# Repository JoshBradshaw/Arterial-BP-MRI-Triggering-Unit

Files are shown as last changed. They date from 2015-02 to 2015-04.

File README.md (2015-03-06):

# Arterial-BP-MRI-Triggering-Unit
Full source code and schematics for an Arterial Blood Pressure Pulse MRI triggering unit

A full description of each major component of this project is available at the [project website](http://joshbradshaw.github.io/Arterial-BP-MRI-Triggering-Unit/)

# This device is an arterial blood presure triggering unit for retrospective gating in MRI imaging.

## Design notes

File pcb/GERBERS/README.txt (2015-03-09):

*.CMP = Top or Component Side
*.SOL = Bottom or Solder Side
*.SLK/PLC = Top/Bottom Component Legend
*.?MK/ST? = Top/Bottom Solder Mask
*.DRD = NC Drill File
*.DRL = Tool Report (sample)
NC Drill File sample	3.3 Leading Zeros is typical

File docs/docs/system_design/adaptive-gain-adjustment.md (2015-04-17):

## Variable Gain Amplifier with SPI Interface

The analog output signal provided by the Samba Sensor’s pressure measurement system had a very small amplitude compared to the full scale range of the analog to digital converter, so an amplifier was required to increase the signal closer to the full scale range of the ADC. 

Unfortunately, the blood pressure of fetal pigs has never been measured from the carotid artery, so it was impossible to determine the correct gain value for the amplifier in advance. This problem was further confounded, because the effect of our chosen anaesthetic on fetal blood pressure was also unknown. To deal with this problem, I opted to build a variable gain amplifier, with an automatic feedback system to maintain a consistent signal amplitude throughout the experiment. A simplified schematic variable gain amplifier circuit is shown below.

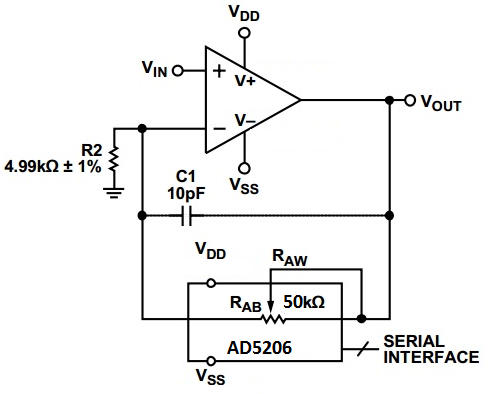
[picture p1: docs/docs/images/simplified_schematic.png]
Simplified schematic


This circuit uses a precision operational amplifier, with a digital potentiometer (AD5206) in the feedback path to allow the gain to be adjusted by the microcontroller as required. The digital potentiometer has 256 counts, giving the amplifier an adjustable gain range of 1-11x. This is sufficient for even the lowest possible fetal blood pressures.

## Algorithm for Gain Adjustment on the Fly

The input of the gain adjustment is a sample from the ADC taken every 100ms. While each sample is recorded, the algorithm compares it to the minimum signal magnitude and maximum magnitude threshold which are 1/5 and 4/5 of the ADC’s full scale range, respectively. After a five second windowing period, the signal amplitude is compared against the thresholds, to see if any gain adjustment is required. The three possible cases:

1.	Signal failed to exceed minimum magnitude threshold during the five second window.
2.	Signal exceeded maximum the maximum magnitude threshold during the five second window.
3.	The signal exceeded the minimum magnitude threshold, and did not exceed the maximum threshold.
    In case one, the gain adjustment algorithm gradually increases the gain during each windowing period, as shown in the figure below. The gain increase stops when the signal exceeds the threshold. Same process occurs in reverse for case three. The algorithm is illustrated in the flow chart below.

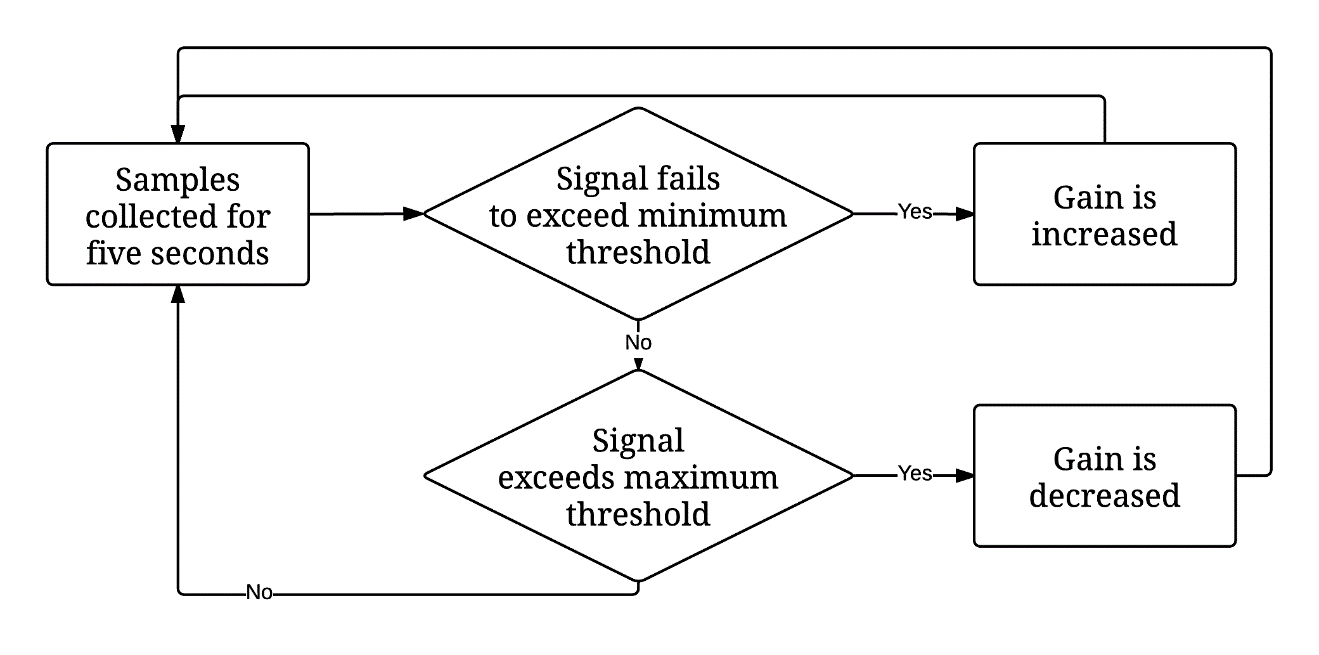
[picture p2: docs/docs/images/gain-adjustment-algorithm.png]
Gain adjustment algorithm flow chart


The actual functioning of the gain adjustment algorithm is illustrated in the plot below. In this test, the triggering system was connected to a function generator which produced a blood pressure waveform with a peak to peak voltage of 700mV. This signal amplitude is based upon recordings on fetal lambs with an identical transducer. As you can see, the gain is very gradually increased in such a manner that it does not disrupt the triggering algorithm, which operates perfectly throughout the duration of the gain increase.

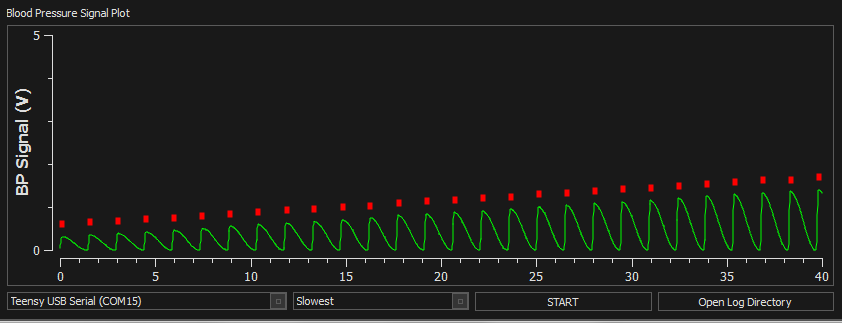
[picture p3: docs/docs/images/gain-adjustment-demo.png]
Gain adjustment demo plot


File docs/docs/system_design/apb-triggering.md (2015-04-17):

## Blood Pressure Signal Preprocessing

The top plot in Figure xx shows an arterial blood pressure waveform which was measured invasively in a fetal lamb. Notice that the notice after the main pressure peak, there is a second reflection peak, which results from closing of the aortic value. 

This waveform is relatively noisy, and the peak is not particularly easy to identify. For this reason, it is necessary to apply a filtering algorithm to simplify peak detection. First a first order low pass filter with a cut-off frequency of 25Hz is applied, to smooth the small spikes in the pressure waveform, as shown in the figure below. The first order low pass filter’s equation is given below.

low pass filter

Next the slow sum function is applied. The slope sum function is defined as:

low pass filter

Where the optimal value of the windowing constant k is the number of samples in the rising edge of the signal [2]. For the fetal pig application, we chose k=15, based upon visual inspection of pre-existing fetal lamb blood pressure recordings, which are very similar to fetal pigs in terms of blood pressure and heart rate. 
The plot below illustrates shows a plot of a fetal lamb’s blood pressure, and the corresponding slope filtered output for that blood pressure waveform. 

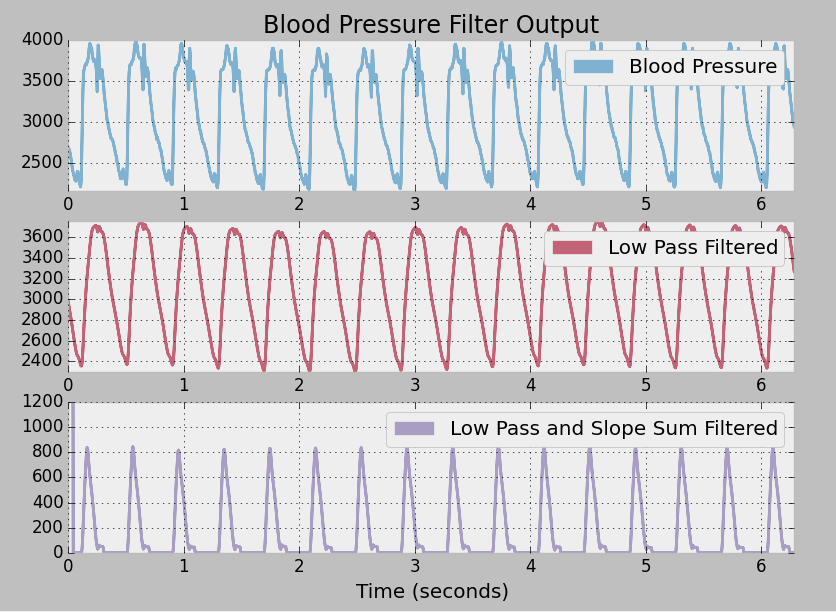
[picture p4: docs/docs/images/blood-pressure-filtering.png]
low pass filter


Notice that the low pass filter removes the high frequency ridges from the blood pressure waveform, leaving only the low frequency content that corresponds to the expansion and contractions of the hearts ventricles. 

The slope sum function improves the signal by establishing a consistent baseline of zero, eliminating the effects of DC drifts in the measurement instrument. The slope sum function also sharpens the peaks, which makes the problem of automatic peak detection far less ambiguous.

## Testing

The algorithm was evaluated against the following test blood pressure waveforms.

1. [MIT Database of non-invasive blood pressure recordings](http://physionet.cps.unizar.es/physiobank/database/slpdb/slpdb.shtml)
2. Pulse oximeter of my own heart, taken while serving as test subject for a maternal health sequence.
3. Invasive fetal lamb blood pressure recordings, taken by an Australian research group.

## Blood Pressure Peak Detection

The blood pressure pulse detection algorithm is a state machine. The high level overview of the algorithm is given by the flow chart below.

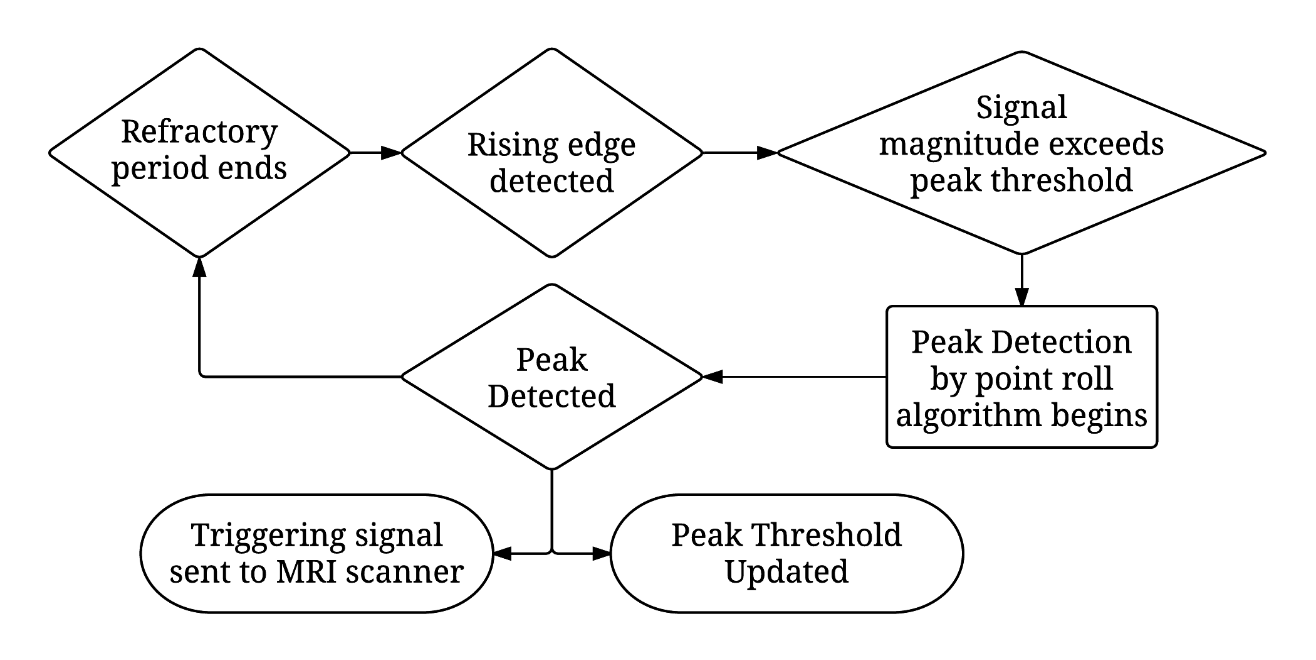
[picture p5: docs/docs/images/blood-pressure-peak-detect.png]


To ensure that the peak detector only triggers on unique blood pressure pulses, a refractory period is applied between peaks, and the algorithm does not begin peak detection until the rising edge is detected and the signal magnitude is greater than the peak threshold. The peak threshold is calculated as ½ of the average of the last five peaks.

The point roll algorithm for peak detection works by comparing the value of the current sample to the value (u[n]) of the fourth more recent sample (u[n-4]). This operation is similar to the backwards approximation of the first derivative. A peak is detected when u[n-4] > u[n], which corresponds to a slow of zero.

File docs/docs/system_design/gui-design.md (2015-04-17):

## Signal Monitoring Tool

The blood pressure triggering device needs to have an interface so that the researcher operating it can tell whether it is functioning properly. The interface must provide the operator with near real-time feedback on the signal level of the pressure sensor, and the timing of the trigger pulses. The interface should provide the researcher with an easy way to export the pressure data for further analysis, and should be sufficiently simple to install on a new computer that it can be quickly transferred via USB key or network drive to a different computer.

The tool is based entirely on [this excellent project](http://www.swharden.com/blog/2013-05-08-realtime-data-plotting-in-python/). All I did was modify the form, integrate the python serial library to get the sensor values from the Teensy over Serial, and add a couple of buttons and menus to control everything. All told, it only amounted to about one day of work. Finally, I used py2exe to make it into a portable application, so that it can be run on any of the computers on the scan room without having to worry about setting up a python environment.

Here's an image of the finished monitoring tool in action.

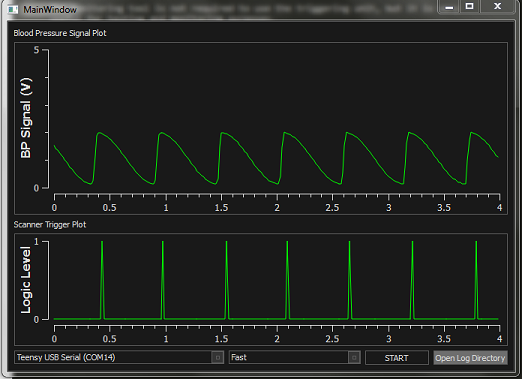
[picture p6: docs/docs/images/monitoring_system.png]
Monitoring System
 

### Setup

There are two ways to run the monitoring tool:

1. On windows you can run the pre-built executable: [monitoring_tool_win32_v1.0.zip](https://drive.google.com/file/d/0B9S2t7PTl3ecVFlvSmQzb3l2UDQ/view?usp=sharing)

2. If that executable doesn't work, the full development environment I built this with can easily be installed. Just download [PythonXY](https://code.google.com/p/pythonxy/), download the the [source code](https://github.com/JoshBradshaw/Arterial-BP-MRI-Triggering-Unit/), navigate to the monitoring_tool directory in terminal and run the program with 

	$ python realtimePlot.py

If you aready have a python 2.X development environment and you don't want to install PythonXY over it, use pip to install pyQt and pySerial.

NOTE: Mac OSX support has not been tested, but this program will most likely run fine on Macs as long as you run from source code (the pre-compiled binary will not work)

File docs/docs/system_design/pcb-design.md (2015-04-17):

## PCB Design

I opted to design a simple PCB for this project, so that more versions of this triggering unit can be produced with minimal effort. 

### Design Criteria

1. Analog ground plane must be completely separated from the digital groundplane to avoid crosstalk on the sensitive analog amplification circuits.
2. Must use 10/10 thou minimum trace width and clearance, so that this board can easily be manufactured by anyone.
3. Must meet the weird drill size restrictions of [APcircuits](http://apcircuits.com/), because they've the only vendor I've who will ship a few boards to SickKids on a quick turnaround for a reasonable price.
4. Must use parts with >1mm pin pitch, so that it can easily be hand assembled by novices.

For anyone wishing to build this board, some moderate to advanced soldering is required. You can do it with very little experience, just follow this tutorial: [Sparkfun SMD soldering tutorial](https://www.sparkfun.com/tutorials/96). Make sure you buy top quality flux, solder and tweezers!

The Teensy eagle CAD library used in this design is available at the [PJRC website](https://www.pjrc.com/teensy/eagle_lib.html). 

### PCB Manufacture

For PCB prototyping, I went with [APcircuits](http://apcircuits.com/). 

Getting one of these boards manufactured is as simple as uploading the GERBER files (included in the git repository) to a manufacturer's website.

### Design:

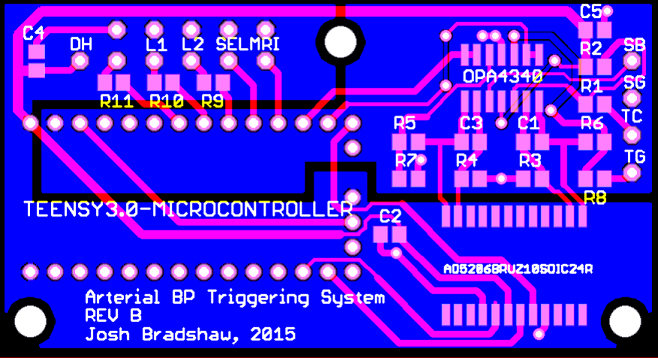
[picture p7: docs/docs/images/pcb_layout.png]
Circuit board layout


### Bare Board:

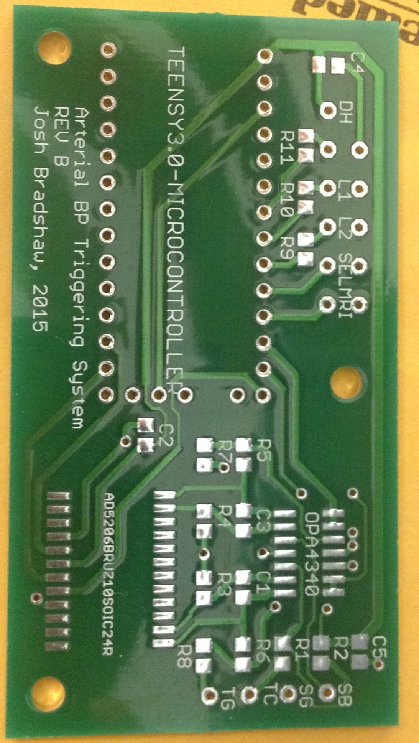
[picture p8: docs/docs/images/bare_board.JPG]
Circuit board layout


### Assembled Board:

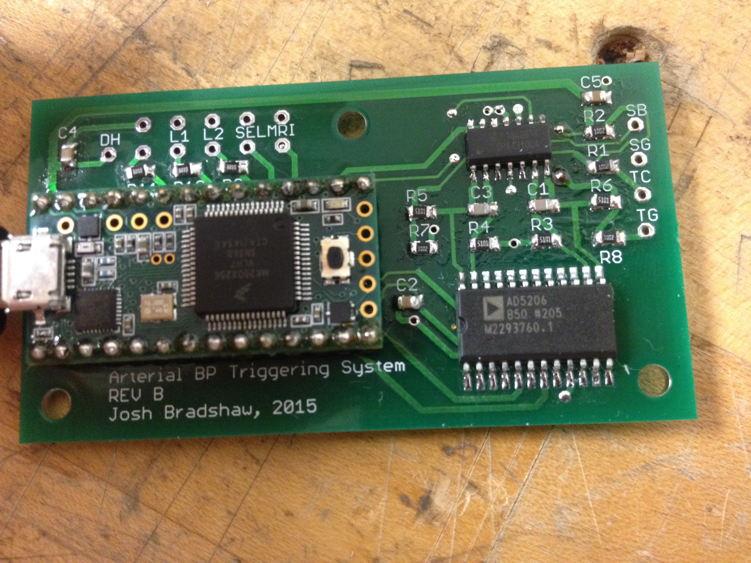
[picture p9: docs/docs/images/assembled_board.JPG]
Circuit board layout


### Things to fix in subsequent revisions

1. One sub-optimal choice I made in the design process of this PCB was the decision to use a 6 channel digital potentiometer, when I'm currently only using two channels. I chose that part simply because I did the breadboard verion with a six channel pot, and because digikey didn't have the 2 or 4 channel version of the part in stock while I was putting the prototype together.

### Related Questions and Uncertainty
1. How much electromagnetic inferferance from the MRI machine will the instruments be exposed to when they're sitting in the control room of the 3T scanner, assuming that we scan with the door closed and the waveguide plugged with a conductive blanket?

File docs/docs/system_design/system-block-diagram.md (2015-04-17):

## System Block Diagram

The blood pressure signal is collected by an optical pressure transducer, which is inserted into the fetal pig’s carotid artery. The optical blood pressure signal is converted into an analog electrical signal by the pressure measurement module (see Appendix A for details), which is then amplified by the variable gain amplifier and measured by the analog to digital converter. 

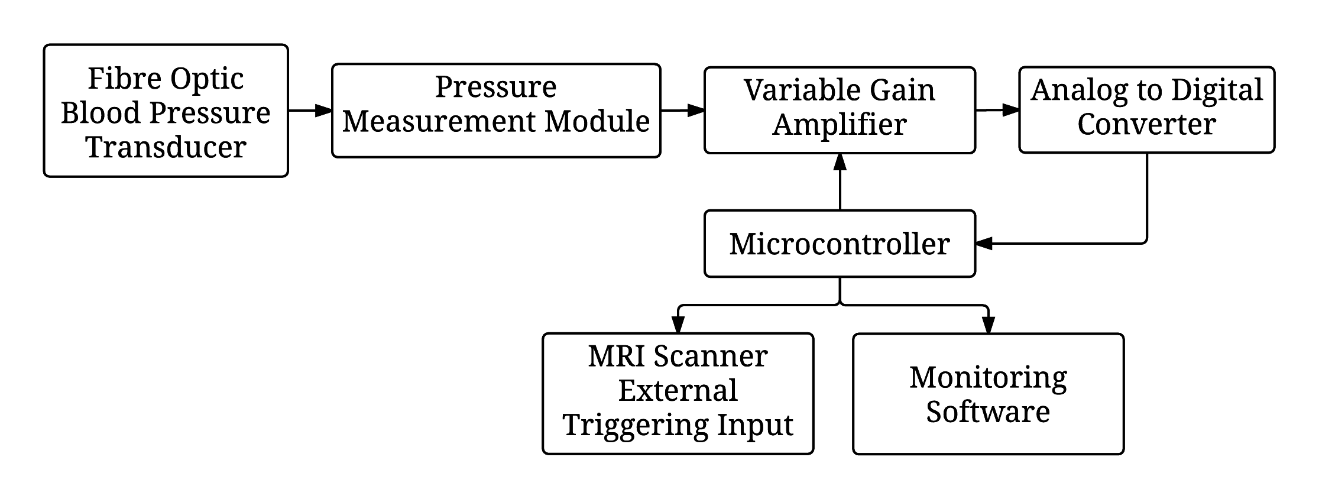
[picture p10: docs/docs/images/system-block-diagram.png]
System block diagram


The microcontroller uses a variety of digital signal processing algorithms to filter the signal and detect the pig’s pulse. Each time a heartbeat is detected, a triggering signal is sent to the MRI scanner, and a signal is sent to the monitoring software so that the experimenter can verify that the triggering signal was sent at the correct instant.

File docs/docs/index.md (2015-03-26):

## System Overview

<style>
td { 
  border: solid;
  border-width: 1px 1px;
  padding: 5px;
}
</style>

The Arterial Blood Pressure Triggering System is an open source tool developed at SickKids. The system converts a blood pressure signal into a TTL signal, as illustrated below.

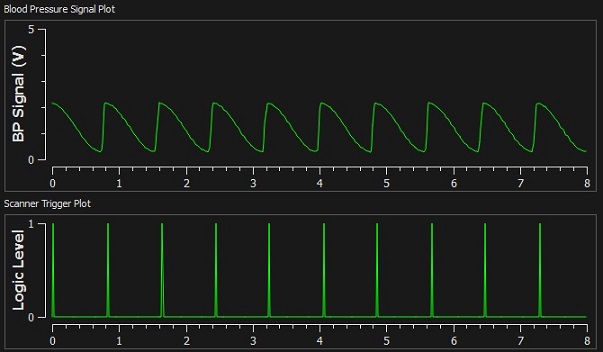
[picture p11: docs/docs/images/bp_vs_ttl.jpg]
illustration of how the triggering system transforms blood pressure signal into TTL signal


This is useful for situations in which a gating signal is required to correct for pulsatile flow or cardiac motion, but the standard clinical ECG or pulse oximeter based triggering systems can not be used. The original application of this system was to provide a retrospective gating signal during 4DFlow and phase contrast scans on prenatal Yorkshire pig fetus's hearts. During the experiments, the fetal pigs blood pressure was monitored using an invasive Samba flow probe in the carotid artery.

### Key Features

* Compatible with [Transonic](http://www.transonic.com/products/research/product/t402t403-multi-channel-research-consoles/) and Samba Sensors pressure measurement modules, and can easily be adapted to work with most other pressure measurement instruments
* Unit calibrates itself automatically every three seconds to correct for baseline drift, and large changes in maximum signal amplitude
* Performs well even on noisy and irregular blood pressure waveforms
* Plug-and-play operation with a one second boot time
* The triggering unit has voltage regulation circuitry complete with inline fuses, to ensure that the scanner will be protected in the event of an electrical fault in the computer or pressure measurement instrument
* Simple monitoring software shows real-time plots of the blood pressure and triggering waveforms, and logs that data so that it can be compared against the scan data in post processing

### Hardware

The triggering unit is shown below:

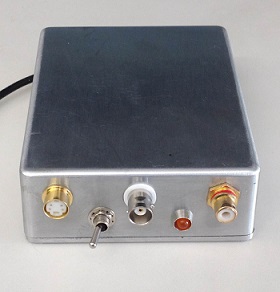
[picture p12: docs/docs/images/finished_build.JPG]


The connections on the front panel of the triggering unit are:

<table>
	<tr>
		<td>Samba Sensor Input (s-video)</td>
		<td>Transonic Sensor Input (BNC)</td>
		<td>External Trigger Out (RCA)</td>
	</tr>
	<tr>
		<td>Input Selection Switch</td>
		<td></td>
		<td>Trigger Status LED</td>
	</tr>
</table>
<br />
Finally, a USB cable runs out of the back corner of the unit. This cable is connected to a computer to power the unit, and optionally to transfer the blood pressure readings to the monitoring software.

## Monitoring Software

triggering unit photo

The monitoring tool give the experimenter real-time feedback on the pressure catheter and the triggering signal. The top chart animation shows the input signal from the pressure catheter, and the bottom chart animation shows the triggering signal that's been sent to the scanner. These charts are updated in real-time with <20ms of delay, so you'll be aware of any irregular heartbeats, or problems with the pressure catheter, right as they happen. Every run of the triggering unit is logged with time and date stamps, so it can be compared with the MRI data in post processing if required.

For more information about the monitoring software see:
1. Monitoring software design

### Scanner compatibility

The SickKids research MRI scanner is the Siemens Magnetom Trio with a field strength of 3T, so the triggering unit's TTL output is calibrated to meet or exceed all of the parameters given in Siemen's timing diagram (taken from the latest version of the Magnetom Trio operating manual). The TTL pulses sent by the unit are 20ms in duration at 3.3V, which should be sufficient for most MRI scanners.

### How to aquire a unit

So far only two of these units have been built, and they were both hand assembled. If you're moderately competant with software and electronics you can build one yourself using the schematics. The parts are listed in the schematics directory, and all of the components are avaialble from digikey. For the PCB board, I may be able to provide you one of my spares. Failing that, you can easily send the GERBER files to any circuit board manufacturer to have them assembled.

Feel free to email me at joshbradshaw11@gmail.com if you are interested in adapting this unit to work with a different blood pressure instrument, or want to commision me to build one for you.

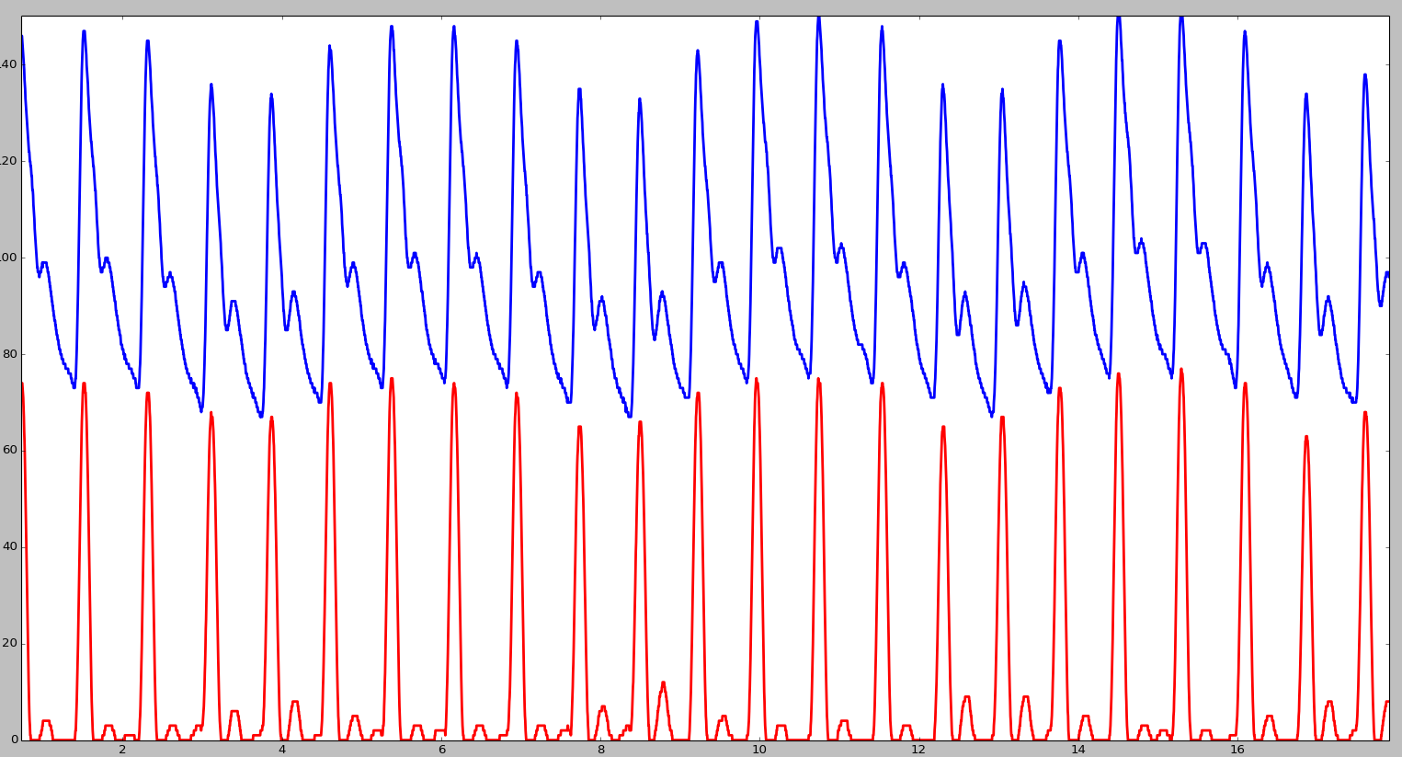
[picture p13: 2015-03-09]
docs/docs/images/ssf_demo.png

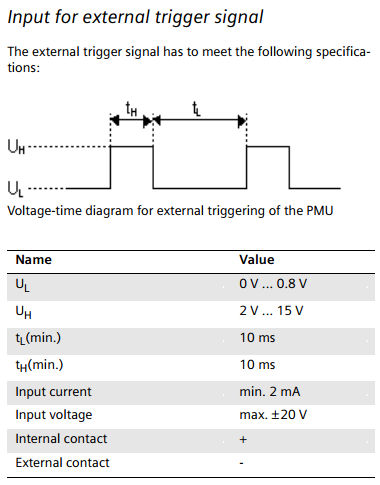
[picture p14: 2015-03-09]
docs/docs/images/siemens_external_trigger (1).png

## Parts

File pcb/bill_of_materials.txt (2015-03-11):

Teensy 3.1 from pjrc.com with header pins
(you can easily solder your old 0.1" headers on if you wish)

part: AD5206BRZ50 package: SOIC-24 quantity: 1
part: OPA4340UA/2K5 package: SOIC-14 quantity: 1

part: 5.1k surface mount resistor package: 0805 quantity: 4
part: 10k surface mount resistor package: 0805 quantity: 4
part: 681 ohm surface mount resistor package: 0805 quantity: 3
part: 10pF surface mount capacitor package: 0805 quantity: 2
part: 0.1uF surface mount capacitor package: 0805 quantity: 3

Other parts (I got these at the hardware store)
A case or project box
SPDT switch
LEDs (must be <3.3V and >5mA max current)
BNC, SVIDEO, RCA connectors (or whatever suits your equipment best)

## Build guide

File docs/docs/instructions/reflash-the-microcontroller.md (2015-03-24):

## How to Reflash the Microcontroller

If for any reason the triggering unit stops working, or requires a software change, you will need to re-flash the Teensy microcontroller. 

To do so:

Install Arduino: [http://arduino.cc/en/Main/Software](http://arduino.cc/en/Main/Software) (I used version 1.6.1)

Install TeensyDuino: [https://www.pjrc.com/teensy/td_download.html](https://www.pjrc.com/teensy/td_download.html)

Connect the triggering unit to your computer's USB port.

Open Windows Device manager and find the Teensy. You will typically find it under ports. 

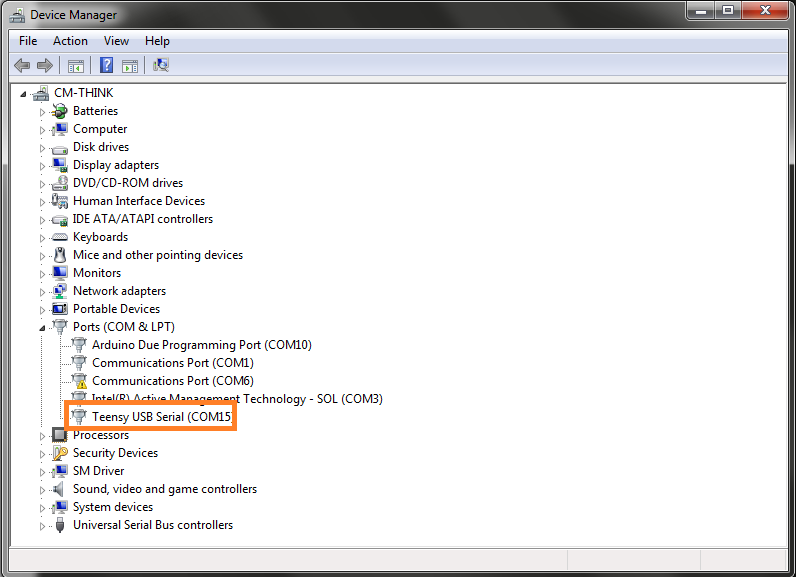
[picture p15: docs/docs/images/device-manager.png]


Note down the COMPORT number (in this case its 15)

Down the source code for the unit from github: [Arterial-BP-MRI-Triggering-Unit](https://github.com/JoshBradshaw/Arterial-BP-MRI-Triggering-Unit)

Next open the Arduino software and open the pressure_trigger_module.ino sketch.

Now you can push your changes to the Teensy microcontroller by pressing VERIFY and then UPLOAD.

Usually this is all you have to do, but sometimes the Teensy requires a manual reset and the software will tell you so by giving you a red error message on the console. If that happens, open the aluminum case (theres a screwdriver that fits perfectly in my drawer) and press the little black button on the teensy board.

If you need to modify my source code there to plenty of resources on the Arduino forum and the Teensy support forum. The language used to program the Arduino boards is essentially C++, without exceptions and other advanced features. 

Note: The contents of the ".ino" file are compiled differently from the .cpp and .h files. Arduino attempts to automatically generate the header file, and this can lead to difficult to understand compilation errors if you use features like classes in this particular source file. For this reason, I recommend putting nothing more than setup(), main() and very basic functions in the ".ino" file.

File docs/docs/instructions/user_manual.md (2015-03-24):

## User Manual

### Setup for Testing with the Analog Function Generator

USE CAUTION! The function generator's output can go up to 20V, which is enough to destroy the pressure trigger module. 
To use it safely:

1. Set the amplitude to minimum and tape it down. Optionally, you can pull the knob out to drop the function generator into the millivolts range.
2. The offset is a little bit tricky to set, because this particular function generator sucks and the offset drifts noticeably from day to day. Pull the knob out engage the switch, and start by setting it to about halfway between 12:00 and 1:00. You can tweak it by a smidgen later to get it just right.
3. To get the waveform looking as close to a arterial blood pressure pulse as possible, set the function to SINE WAVE the frequency range to 10Hz, pull the symmetry knob out to engage it and twist counter-clockwise to the stop. Finally, set the frequency selector knob to 0.2 (for 120 BPM), and leave sweep turned off.
4. At this point you can either use the BNC -> S-video adapter that I made to connect to the Samba input, or a standard BNC cable to connect to the Transonic input.
5. Follow steps 7-9 of the Samba instructions and test the device.

The photo below illustrates the setup, as well as the correct positioning of the knobs on the function generator.

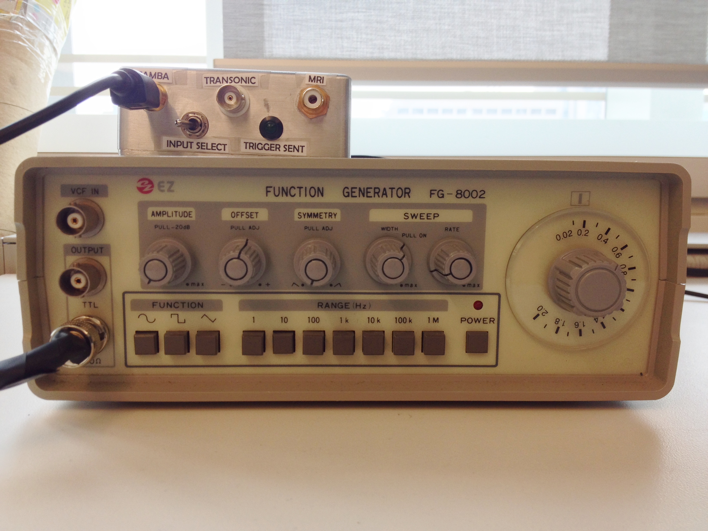
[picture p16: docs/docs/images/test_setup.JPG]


### Setup for Samba 202 Pressure Measurement System

If this is your first time handling the Samba probes, take the time to read the relevant sections of the Samba user manual (included in the box). For invasive measurements you will require distiled and de-ionized water for cleaning the transducer tip, which you can obtain from the wet lab on the 8th floor of the Peter Gilgan Center for Research and Learning (the dispenser is a blue nozzle attached to the main sink). Sterile glassware is available in the hallway that separates the dry lab from the wet lab, you're free to take what you need as long as you return it to the same station for washing.

1. Power up the Samba 202, it will take 1-3 minutes to stabilize the internal temperature.
2. Connect the Samba pressure sensor to channel TWO of the pressure measurement system. Press firmly, because hearing a click does not necessarily mean that a good connection has been made. Be very careful to only handle the blue plastic connector and not the black stress relief on the cable. The fragility of these sensors can not be overstated. The reason we have to use channel two is that channel one is unreliable for unknown reasons, connector contamination is a possibility.
3. Once the Samba unit recognizes the transducer press 1 to zero the transducer. The transducer should be zeroed in free air so that both the low and high blood pressures will give a positive pressure reading.
4. At this point the Samba unit should be working properly and continuously measuring pressure. If you encounter a bad connection error or something along those lines check the manual for instructions. Now is the ideal time to insert the pressure transducer into the test subject.
5. Connect the analog output of the Samba pressure sensor to the pressure trigger module using the S-Video cable provided (this cable has a transparent housing). The connection is labeled SAMBA.
6. Ensure that the INPUT SELECT toggle switch is in the left position (facing the SAMBA input connector).
7. Use the 25ft RCA cable to connect the trigger unit to the external trigger input on the MRI scanner. The external trigger input is on the left side of the scanner, and is marked with a little arrow directed inwards.
8. Plug the USB cable attached to the pressure trigger module to a computer. Ensure that the computer is plugged in (not just running on battery). This is important, because not all laptops maintain a steady 5V USB voltage when they're running on battery power.
9. Launch "realtimePlot.exe" on the computer.
10. Use the serial port selector (dropdown menu on bottom left corner) and choose the port called Teensy USB Serial.
11. Press Start and watch to see whether the system is triggering as expected.

The photo below illustrates most of the connections that you will need to make, as well as the screen that you should see when the Samba pressure measurement system is functioning properly.
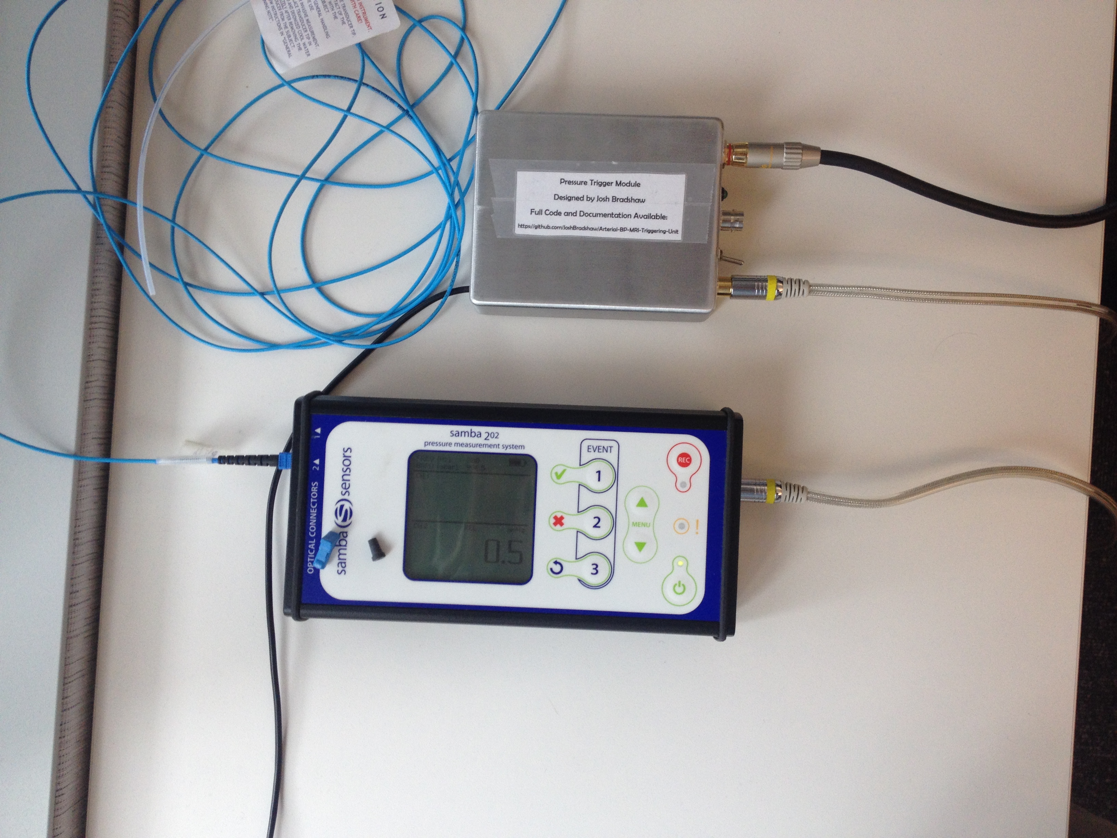
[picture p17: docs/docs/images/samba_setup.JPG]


NOTE: The Samba sensors module is powered by USB, and has an internal battery. The battery should last for more than an hour of sustained used, but the unit is old enough that it can not be counted on. The easiest way to power the unit is via USB, (I searched many hardware stores for the DC jack that would fit the 5V input, with no success). A standard 2.5W (5V/500mA) USB power supply (which is the output of a standard computer, laptop or iPhone wall wart) does not provide enough power to keep the unit from running dead. Its possible that connecting the Samba device to a higher wattage USB power supply such as an iPad charger may keep it running steadily.

### Setup for Transonic TS420 Perivascular Flow Module

Note: I never actually had access to a TS420 during the design or testing of this instrument. I used the user manual of the device to get the relevant specifications and designed and tested the device based upon the manufacturer's description of its typical behavior. Thus, I can not guarantee that these instructions are complete, or that the device will work properly with the triggering system, especially if Transonic comes out with a new version.

1. Follow Transonic's instructions for setting up their flow measurement system.
2. Connect the flow measurement system to the the TRANSONIC input connector on the pressure trigger module using a standard BNC cable (our lab already has two short BNC cables, longer cables are available from Active Surplus or monoprice.com if required).
3. Ensure that the input selection toggle switch is in the right position (facing the Transonic connector)
4. Follow steps 7-9 of the Samba instructions.

### Troubleshooting

1. As with all electronics, if you have trouble with the device start with unplugging it and plugging it back in.
2. The device only reads the value of the input selection switch once during startup, so the switch must be in the correct position BEFORE the pressure trigger module is powered up.
3. The RCA connectors on the scanner are recessed and poorly placed, we've had trouble getting a good connection with the cable before. If there is any discrepancy between what the monitoring tool shows and the scanner's external triggering display, triple check the cables. If the RCA cable has any visible damage, replace it ($7 at Active Surplus) because even minor sheath damage will have serious consequences on the cable's ability to pass signal in the MR environment.
4. The LED I wired into the device was of questionable quality, don't worry it stops working. You will still be able to use the monitoring software to see when the trigger signal has been sent.
5. BNC connectors only make a good connection when the little thumb-turn sleeve is locked in place, double check them every time.

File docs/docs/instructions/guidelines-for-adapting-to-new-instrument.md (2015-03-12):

## Guidelines for Adapting the Pressure Trigger Module to Work with a new Sensor/Instrument

The Arterial BP Triggering System should be fairly easy to adapt to a new pressure measurement system. 

### Instruments with Analog Outputs

As it stands, the pressure trigger module has two analog inputs:

1. One 0-5V analog input for the Samba Sensors pressure measurement system. (connected to signal pin SB and ground pin SG on the circuit board)
2. One -5-5V analog input for the Transonic pressure measurement system. (connected to signal pin TC and ground pin TG on the circuit board)

If the pressure measurement system you wish to work with has an analog output less than or equal to either of these voltage ranges, then you're golden. Just cut the wires off of the connector. Do this carefully so that you can reuse the wires and avoid the painful process of de-soldering the wires from the PCB. 

This video will teach you everything you need to know about soldering: [Dave Jones Through Hole Soldering Tutorial](https://www.youtube.com/watch?v=fYz5nIHH0iY)

Examples: 

1. An instrument with an analog voltage output -2-2V could be connected to the Transonic input
2. An instrument with an analog voltage output of 0-3V could be connected to the Samba input.

If the instrument has an output voltage range greater than either of these inputs, then all is not lost. Just add a [voltage divider](http://en.wikipedia.org/wiki/Voltage_divider) between the instrument and the pressure trigger module's analog input. Choose resistors in the 10-100Kohm resistance range to avoid loading down the instrument and you'll be golden.

### Instruments with Digital Outputs

If the instrument only has a digital output available, then this problem will be more advanced. The internal circuitry and microcontroller code will need to be modified. Feel free to get in touch with me at joshbradshaw11@gmail.com with details about the instrument and I will help you.

If you wish to do the modifications to the circuit and PCB yourself, then everything you will need is in the eagle project files in the repository. Tons of useful information about interfacing the pressure trigger module's [Teensy3.1](https://www.pjrc.com/teensy/teensy31.html) microcontroller using various digital communications protocols is available on the [support forum](https://forum.pjrc.com/forum.php).

### Notes

1. If you need access to electronics test equipment beyond what is avaialable at SickKids, go to the mouse imaging cetner (MiCE) in the Toronto Center for Phenogenetics. Sharon Portney can get you access for the day. Bring your own parts 
2. Most connectors are available from the basement of the home hardware at College/Spadina or Active Surplus on Queen St. W. Failing that, order from digikey.com.

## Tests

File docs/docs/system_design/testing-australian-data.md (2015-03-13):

## Testing Against Fetal Lamb BP Data

Dr. Jonathan Mynard of Australia was kind enough to provide me with three ~30 second invasive pressure catheter recordings taken in a fetal lamb. These recordings are slightly unusual, because they have extra systolic beats, which lead to little skips in the waveform. These recordings are a useful analog for the fetal pig pressure waveform, because pigs are also prone to extra systolic beats, and fetal lambs and fetal pigs have similar fetal heart rates.

To test these values, I used an Arduino Due as a waveform generator, and generated a 1-3V signal, which I then divided down to 0.5-1V

Information about the heart rate of a sedated fetal pig in this paper: http://jap.physiology.org/content/90/4/1577 [Effects of morphine and naloxone on fetal heart rate and movement in the pig](http://jap.physiology.org/content/90/4/1577)

Test results:

Data File 1:

Here's a zoomed in snapshot of the triggering system operating on a fetal lamb:

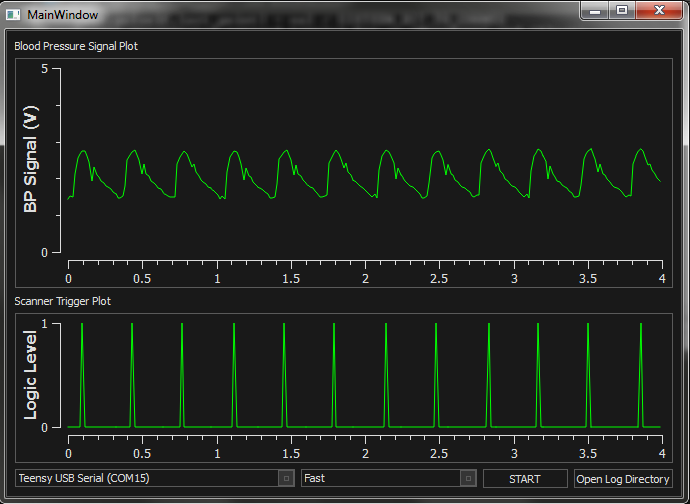
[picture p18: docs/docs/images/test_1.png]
image of an arterial blood pressure pulse with its corresponding trigger signal below


Here's a section of the fetal lamb's blood pressure trace that has a skip beat, which are common in both lambs and pigs:

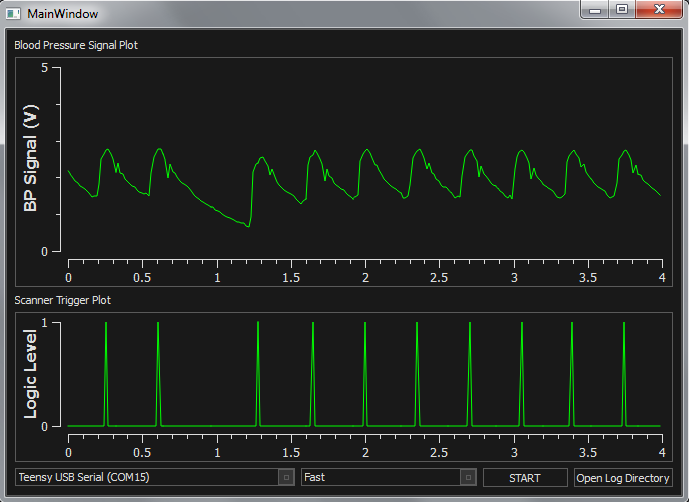
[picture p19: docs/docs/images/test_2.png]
image of an arterial blood pressure pulse with its corresponding trigger signal below


This zoomed out view shows the 30s pulse waveform

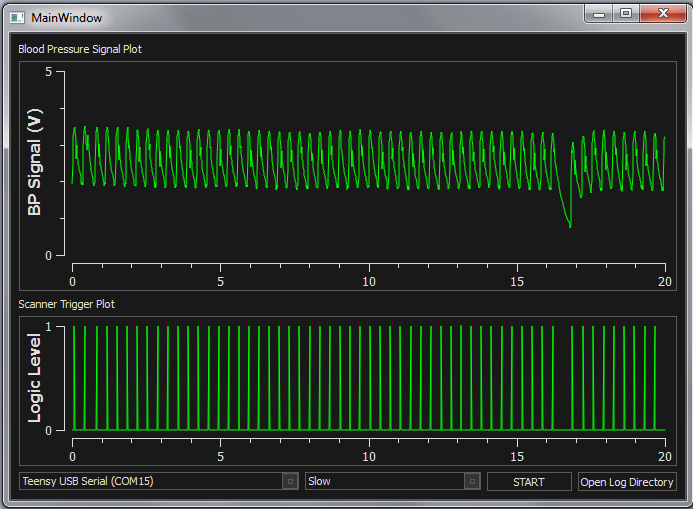
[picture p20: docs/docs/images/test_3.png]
image of an arterial blood pressure pulse with its corresponding trigger signal below


I ran tests like these on a variety of different pulse pressure waveforms, on lamb data, human data, pulse oximeter recordings of my own heart, and simulated arterial blood pressure pulses that I generated using an arbitrary function generator. The pressure trigger unit performed excellently with all of the little variations in waveform shape, magnitude, offset drift and frequencies. I'm very content with the results.

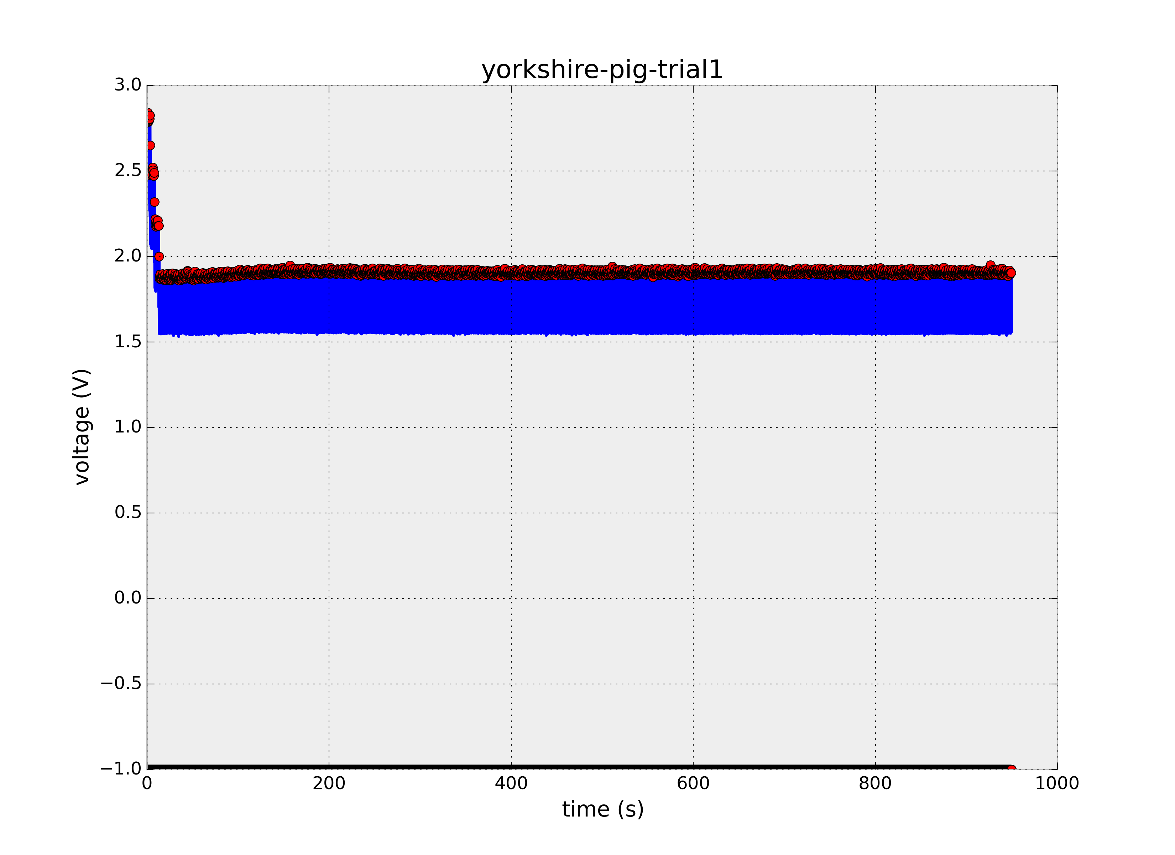
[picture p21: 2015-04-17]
data_analysis/test.png

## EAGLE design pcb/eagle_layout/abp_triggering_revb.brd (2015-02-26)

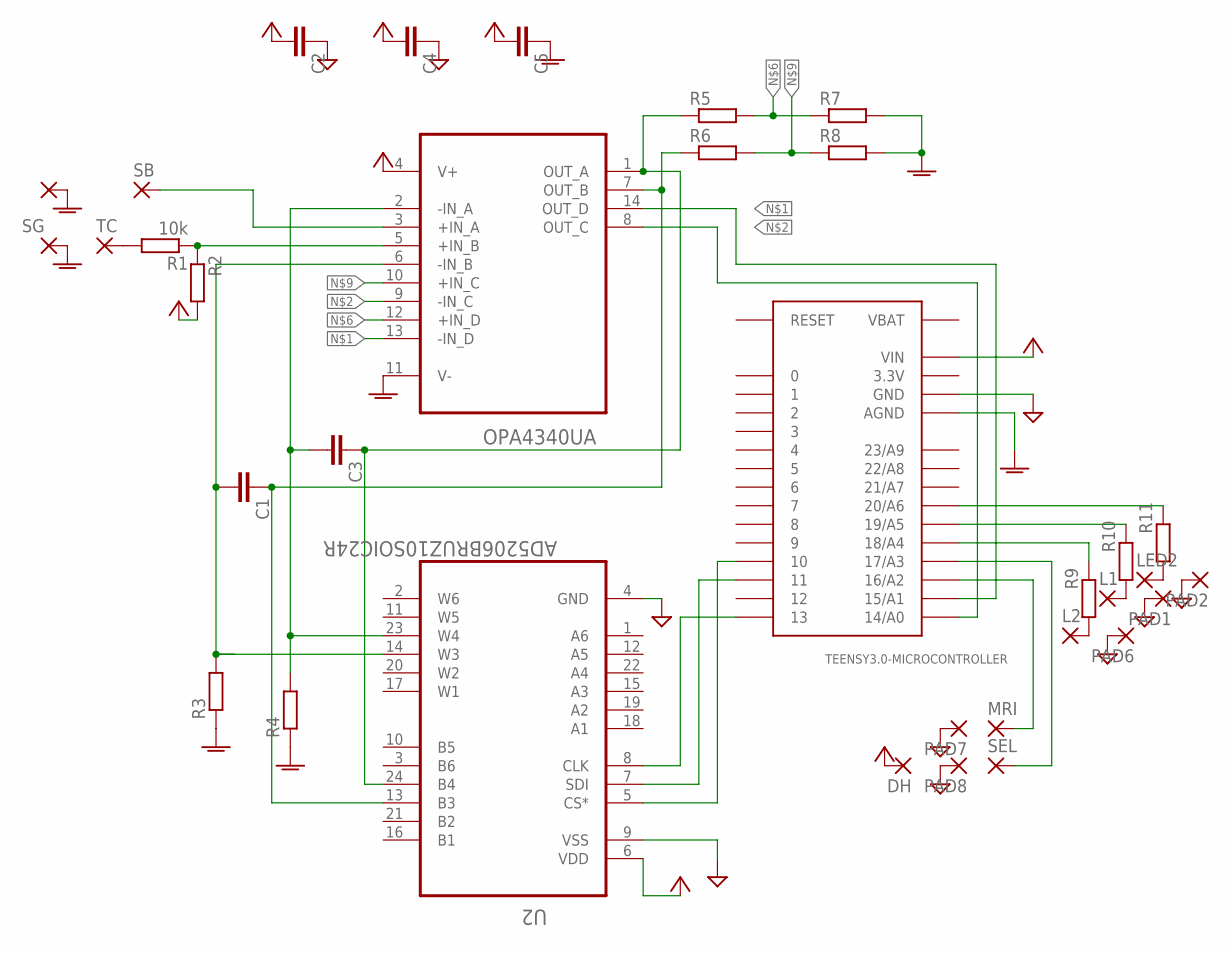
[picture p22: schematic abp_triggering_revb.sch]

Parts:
C1, C3: 10pF; C0805
C2, C4, C5: 0.1uF; C0805
DH: WIREPAD1,6/0,9; 1,6/0,9
L1, L2: WIREPAD1,6/0,9; 1,6/0,9
LED2: WIREPAD1,6/0,9; 1,6/0,9
MRI: WIREPAD1,6/0,9; 1,6/0,9
PAD1, PAD2, PAD6, PAD7, PAD8: WIREPAD1,6/0,9; 1,6/0,9
R1, R2: 10k; R0805
R3, R4: 5k; R0805
R5, R6: 12k; R0805
R7, R8: 23.2k; R0805
R9, R10, R11: 681; R0805
SB: SAMBA; 1,6/0,9
SEL: WIREPAD1,6/0,9; 1,6/0,9
SG: WIREPAD1,6/0,9; 1,6/0,9
TC: WIREPAD1,6/0,9; 1,6/0,9
TEENSY3.0-MICROCONTROLLER: TEENSY_3.0_BASIC-PGM
TG: WIREPAD1,6/0,9; 1,6/0,9
U1: OPA4340UA; SOIC127P600X175-14N
U2: AD5206BRUZ10SOIC24R; SO24R

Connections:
3.3V: TEENSY3.0-MICROCONTROLLER.3.3V, TEENSY3.0-MICROCONTROLLER.3.3V1 (3.3V)
AGND: C5.1, R3.1, R4.1, R7.2, R8.2, SG.1, TEENSY3.0-MICROCONTROLLER.AGND, TG.1, U1.11 (V-)
GND: C2.1, C4.1, PAD1.1, PAD2.1, PAD6.1, PAD7.1, PAD8.1, TEENSY3.0-MICROCONTROLLER.GND, TEENSY3.0-MICROCONTROLLER.GND1 (GND), U2.4 (GND), U2.9 (VSS)
unnamed: TEENSY3.0-MICROCONTROLLER.15/A1, U1.13 (-IN_D), U1.14 (OUT_D)
unnamed: TEENSY3.0-MICROCONTROLLER.14/A0, U1.8 (OUT_C), U1.9 (-IN_C)
unnamed: C3.2, R4.2, U1.2 (-IN_A), U2.23 (W4)
unnamed: R1.1, R2.1, U1.5 (+IN_B)
unnamed: C3.1, R5.1, U1.1 (OUT_A), U2.24 (B4)
unnamed: R5.2, R7.1, U1.12 (+IN_D)
unnamed: TEENSY3.0-MICROCONTROLLER.10, U2.5 (CS*)
unnamed: TEENSY3.0-MICROCONTROLLER.11, U2.7 (SDI)
unnamed: R6.2, R8.1, U1.10 (+IN_C)
unnamed: SB.1, U1.3 (+IN_A)
unnamed: L2.1, R9.1
unnamed: C1.2, R3.2, U1.6 (-IN_B), U2.14 (W3)
unnamed: R1.2, TC.1
unnamed: R9.2, TEENSY3.0-MICROCONTROLLER.18/A4
unnamed: MRI.1, TEENSY3.0-MICROCONTROLLER.16/A2
unnamed: SEL.1, TEENSY3.0-MICROCONTROLLER.17/A3
unnamed: C1.1, R6.1, U1.7 (OUT_B), U2.13 (B3)
unnamed: L1.1, R10.1
unnamed: TEENSY3.0-MICROCONTROLLER.13, U2.8 (CLK)
unnamed: R10.2, TEENSY3.0-MICROCONTROLLER.19/A5
unnamed: LED2.1, R11.1
unnamed: R11.2, TEENSY3.0-MICROCONTROLLER.20/A6
VBAT: TEENSY3.0-MICROCONTROLLER.VBAT
VCC: C2.2, C4.2, C5.2, DH.1, R2.2, TEENSY3.0-MICROCONTROLLER.VIN, U1.4 (V+), U2.6 (VDD)

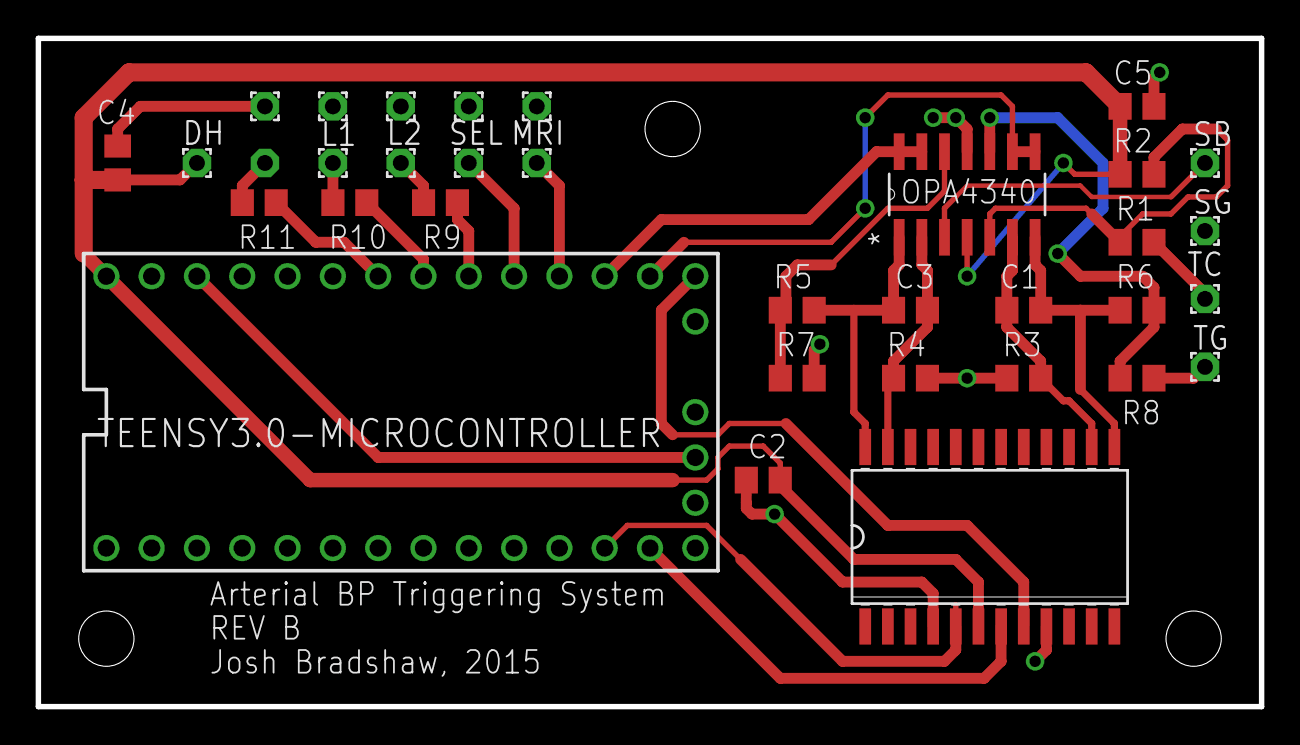
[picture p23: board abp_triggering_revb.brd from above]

Board: 2 copper layers, 68.6 x 37.5 mm, 34 parts (1 on the bottom side), 26 nets.

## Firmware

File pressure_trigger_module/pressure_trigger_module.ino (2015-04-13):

#include "IntervalTimer.h"
#include "PressurePeakDetect.h"
#include "AutoGainAdjust.h"

IntervalTimer sampletimer;

// written for Teensy 3.1 running at 96 MHz

const int SAMPLING_PERIOD = 4; // milliseconds
const int TRIGGER_PULSE_DURATION = 20; // milliseconds, given in the scanner's external triggering timing table
const int SCANNER_TRIGGER_PIN = 19;
const int LED_PIN = 18;

const int PULSE_DURATION = TRIGGER_PULSE_DURATION / SAMPLING_PERIOD;
const int GAIN_ADJUST_PERIOD = 100; // milliseconds
volatile int gainAdjustDuration = GAIN_ADJUST_PERIOD / SAMPLING_PERIOD;
volatile int pulseDurationCount;
volatile int gainAdjustCount = 0;
volatile bool triggerPulseHigh = false;

volatile int ANALOG_INPUT_PIN; // set at startup depending on switch position
volatile int serial_update_count = 0;
const int SAMPLE_SEND_PERIOD = 3;
volatile int sampleSendCount = 0;

lowPassFilter filt;
slopeSumFilter ssf;
peakDetect pd;

void setup() {
    Serial.begin(115200); // fastest stable BAUD rate (Hz)
    analogReadRes(16);  // the teensy has 16 bit ADCs
    pinMode(SCANNER_TRIGGER_PIN, OUTPUT);
    pinMode(LED_PIN, OUTPUT);
    pinMode(INPUT_SELECT_PIN, INPUT);

    bool analogInputSelect = digitalRead(INPUT_SELECT_PIN);

    if(analogInputSelect) { // switch right --> transonic
        ANALOG_INPUT_PIN = 14;
    } else { // switch left --> samba
        ANALOG_INPUT_PIN = 15;
    }

    // hardware clock interrupt service routine calls the sample routine every x microseconds
    sampletimer.begin(sample, SAMPLING_PERIOD * 1000);
    setupGainAdjustment();
}

void loop() {

}

void sample() {
    // signal pathway
    // blood pressure transducer --> Arduino ADC --> low pass filter --> slopesum function --> peak detector
    int sampleVal = analogRead(ANALOG_INPUT_PIN);
    int lpfVal = filt.step(sampleVal);
    int ssfVal = ssf.step(lpfVal);
    bool sampleIsPeak = pd.isPeak(ssfVal);

    if(sampleIsPeak) {
        // when a peak is detected, sent a TTL pulse to the scanner
        digitalWrite(SCANNER_TRIGGER_PIN, HIGH);
        digitalWrite(LED_PIN, HIGH);
        triggerPulseHigh = true;
        pulseDurationCount = 0;
    }

    if (triggerPulseHigh && pulseDurationCount >= PULSE_DURATION) {
        // keep the TTL pulse at logic high (3.3V) until pulse duration exceeded 
        digitalWrite(SCANNER_TRIGGER_PIN, LOW);
        digitalWrite(LED_PIN, LOW);
        triggerPulseHigh = false;
    } else if (triggerPulseHigh) {
        pulseDurationCount++;
    } else {
    }

    if (gainAdjustCount >= gainAdjustDuration) {
        adjustGain(sampleVal);
        gainAdjustCount = 0;
    } else {
        gainAdjustCount++;
    }
    // send data to the plotting/logging program
    if (sampleSendCount < SAMPLE_SEND_PERIOD) {
        sampleSendCount += 1;
    } else {
        Serial.printf("%d %d\n", sampleVal, triggerPulseHigh);
        sampleSendCount = 0;
    }
}

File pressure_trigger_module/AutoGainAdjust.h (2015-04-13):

/*
 This code adjusts the gain of a non-inverting amplifier to bring a pressure
 sensor's signal level into the ideal range for measurement with the
 Teensy microntroller's ADC.

 The AD5206 is SPI-compatible,and to command it, you send two bytes,
 one with the channel number (0 - 5) and one with the resistance value for the
 channel (0 - 255).

 LMC6464 is an instrumentation grade micropower rail-to-rail op-amp

 The circuit:
 AD5206
  * CS - to digital pin 10  (SS pin) on Teensy
  * SDI - to digital pin 11 (MOSI pin) on Teensy
  * CLK - to digital pin 13 (SCK pin) on Teensy
 LMC6464
  * IN (-) A - connected to B3 on AD5206
  * IN (+) A - connected to Samba Sensor's analog signal output
  * OUT A - connected to W3 on AD5206 and pin 14 on Teensy

*/

#ifndef __AUTOGAINADJUST__
#define __AUTOGAINADJUST__

#include "spi4teensy3.h"

// set pin 10 as the slave select for the digital pot:
const int slaveSelectPin = 10;
const int INPUT_SELECT_PIN = 17;

volatile int GAIN_POT;

// these numbers are based on a 16 bit ADC which has 2^16 = 65536 counts
const int MIN_SIGNAL_AMPLITUDE = 25000; // ~0.76 V from the noninverting amplifier
const int TARGET_AMPLITUDE = 35000;
const int MAX_SIGNAL_AMPLITUDE = 55000; // ~4.20 V from the noninverting amplifier
// number of potentiomter codes to correct by if signal is out of range
// a higher number results in a faster correction, at the risk of over-adjusting to short term amplitude spikes
const int CORRECTION = 5;

volatile int potentiometerValue = 0; // range 0-256 where 0 -> ~84 ohms and 256 -> ~50 k-ohms
// if gain is being shifted up or down, this gives the stopping value
volatile int targetPotentiometerValue = potentiometerValue;

const int WINDOW_PERIOD = 45; // 50 x 100ms = 5s
volatile int windowCount = 0; // gain is adjusted when windowCount exceeds WINDOW PERIOD

volatile bool minExceeded = false;
volatile bool maxExceeded = false;
volatile bool targetExceeded = false;

// 0 = equilibrium
// 1 = increasing gain to meet threshold
// 2 = decreasing gain to meet threshold
// starts in increasing state to ensure that the signal is amplified to an optimal level at startup
volatile int seekState = 1;

void digitalPotWrite(const int address, int value) {
    // write the new potentiometer value to the digital pot chip through SPI
    // take the SS pin low to select the chip:
    digitalWrite(slaveSelectPin, LOW);
    //  send in the address and value via SPI:
    spi4teensy3::send(address);
    spi4teensy3::send(potentiometerValue);
    // take the SS pin high to de-select the chip:
    digitalWrite(slaveSelectPin, HIGH);
}

void setupGainAdjustment() {
    bool analogInputSelect = digitalRead(INPUT_SELECT_PIN);
    if (analogInputSelect) {
        GAIN_POT = 2; // transonic signal pathway is connected to B3 and W3 which is pot 2 (zero indexing)
    } else {
        GAIN_POT = 3; // samba signal pathway
    }

    pinMode (slaveSelectPin, OUTPUT);
    spi4teensy3::init(); // the teensy has a hardware SPI module, this sets it up
    digitalPotWrite(GAIN_POT, 0); // start with unity gain to avoid clipping
}

// algorithm:
// have minimum maximum and target signal threshold
// during a 5 second window signal must exceed minimum and not exceed maximum
// if the signal doesn't meet these criteria, it will be increased or decreased until its max
// ampitude passes TARGET_AMPLITUDE, or the amplifier reaches maximum or minimum gain
void adjustGain(const int sensor_value) {
    // adjust potentiometer value if required (done in steps of 1 count for smoothness)

    // increase the pot value by one count
    if (potentiometerValue < targetPotentiometerValue) {
        potentiometerValue += 1;
        digitalPotWrite(GAIN_POT, potentiometerValue);
    }
    // decrease the pot value by one count
    if (potentiometerValue > targetPotentiometerValue) {
        potentiometerValue -= 1;
        digitalPotWrite(GAIN_POT, potentiometerValue);
    }

    // check if this sample is out of bounds
    if (sensor_value > MIN_SIGNAL_AMPLITUDE) {
        minExceeded = true;
    }
    if (sensor_value > MAX_SIGNAL_AMPLITUDE) {
        maxExceeded = true;
    }
    if (sensor_value > TARGET_AMPLITUDE) {
        targetExceeded = true;
    }
    // this section runs every 5 seconds
    // checks if gain needs to be adjusted, and sets the new gain value if required
    if (windowCount > WINDOW_PERIOD) {
        // check if min or max have been violated
        if (!minExceeded) {
            seekState = 1;
        }
        if (maxExceeded) {
            seekState = 2;
        }
        // if unit was increasing gain, check if the threshold magnitude was reached
        if (seekState == 1) {
            if (targetExceeded) {
                seekState = 0;
            } else if (potentiometerValue <= 256 - CORRECTION) {
                targetPotentiometerValue += CORRECTION;
            }
            else {
                return;
            }
        }
        // if unit was decreasing gain, check if threshold reached
        if (seekState == 2) {
            if (!targetExceeded) {
                seekState = 0;
            } else if (potentiometerValue > 0 + CORRECTION) {
                targetPotentiometerValue -= CORRECTION;
            } else {
                return;
            }
        }
        // reset state
        minExceeded = false;
        targetExceeded = false;
        maxExceeded = false;
        windowCount = 0;
    }
    windowCount++;
}

#endif

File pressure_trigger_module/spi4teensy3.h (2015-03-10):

/*
 * File:   spi4teensy3.h
 * Author: xxxajk
 *
 * Created on November 21, 2013, 10:54 AM
 */

#ifndef SPI4TEENSY3_H
#define	SPI4TEENSY3_H
#if defined(__MK20DX128__) || defined(__MK20DX256__)
#include <mk20dx128.h> // same header for Teensy 3.0 & 3.1
#include <core_pins.h>
#include <sys/types.h>

#ifndef SPI_SR_RXCTR
#define SPI_SR_RXCTR 0XF0
#endif
#ifndef SPI_PUSHR_CONT
#define SPI_PUSHR_CONT 0X80000000
#endif
#ifndef SPI_PUSHR_CTAS
#define SPI_PUSHR_CTAS(n) (((n) & 7) << 28)
#endif

#define SPI4TEENSY3_MODE_0 0, 0
#define SPI4TEENSY3_MODE_1 0, 1
#define SPI4TEENSY3_MODE_2 1, 0
#define SPI4TEENSY3_MODE_3 1, 1
#define MODE_TO_SPI4TEENSY3_MODE(x) (x & 1), (x&2)

namespace spi4teensy3 {
void init();
void init(uint8_t speed);
void init(uint8_t cpol, uint8_t cpha);
void init(uint8_t speed, uint8_t cpol, uint8_t cpha);
void send(uint8_t b);
void send(void *bufr, size_t n);
uint8_t receive();
void receive(void *bufr, size_t n);

//void updatectars();
};
#endif /* __MK20DX128__ || __MK20DX256__ */
#endif	/* SPI4TEENSY3_H */

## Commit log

2015-02-13 working teensy implementation of triggering algorithm that ran stable for 16 hours
2015-02-19 first revision of schematic
    [first_draft_schematic.brd, first_draft_schematic.sch]
2015-02-20 routed REV A of the board, silkscreen not yet done
    [clean_with_no_autoroute.brd, first_draft_schematic.brd, first_draft_schematic.sch]
2015-02-21 updated board fixed labels
    [first_draft_schematic.brd, first_draft_schematic.sch]
2015-02-23 new board layout
    [clean_with_no_autoroute.brd, first_draft_schematic.brd, first_draft_schematic.sch]
2015-02-23 made finishing touching to the boards silkscreen and fattenned up the traces where I could
    [first_draft_schematic.brd, first_draft_schematic.sch]
2015-02-23 schematic before package switch
    [first_draft_schematic.brd, first_draft_schematic.sch]
2015-02-24 finalized board layout
    [first_draft_schematic.brd, first_draft_schematic.sch]
2015-02-26 ditched all the useless eagle metadata files
    [first_draft_schematic.DRL]
2015-03-04 device fully functional, input selection feature added
2015-03-04 got GUI prototype working
2015-03-04 GUI prototype working
2015-03-05 refactored and wired up the UI
2015-03-10 renamed directories
    [first_draft_schematic.brd, first_draft_schematic.sch]
2015-03-10 made a really simple bill of materials
    [first_draft_schematic.brd, first_draft_schematic.sch]
2015-03-11 cleaned up eagle directory, name things sensibly
    [first_draft_schematic.brd, first_draft_schematic.sch]
2015-03-11 renamed eagle project
    [abp_triggering_revb.brd, abp_triggering_revb.sch]
2015-03-26 state before trying to sensor working
2015-04-07 filter and ssf working awesome, something weird with peak detection using new filter
2015-04-07 fixed sample buffering
